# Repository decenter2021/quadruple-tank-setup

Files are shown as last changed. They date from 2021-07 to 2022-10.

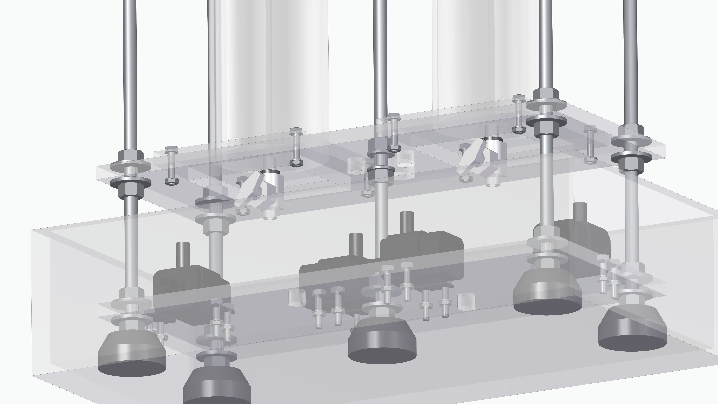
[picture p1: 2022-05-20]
cad-quadruple-tank/renders/quadruple_tank_assembly_render_10.jpg

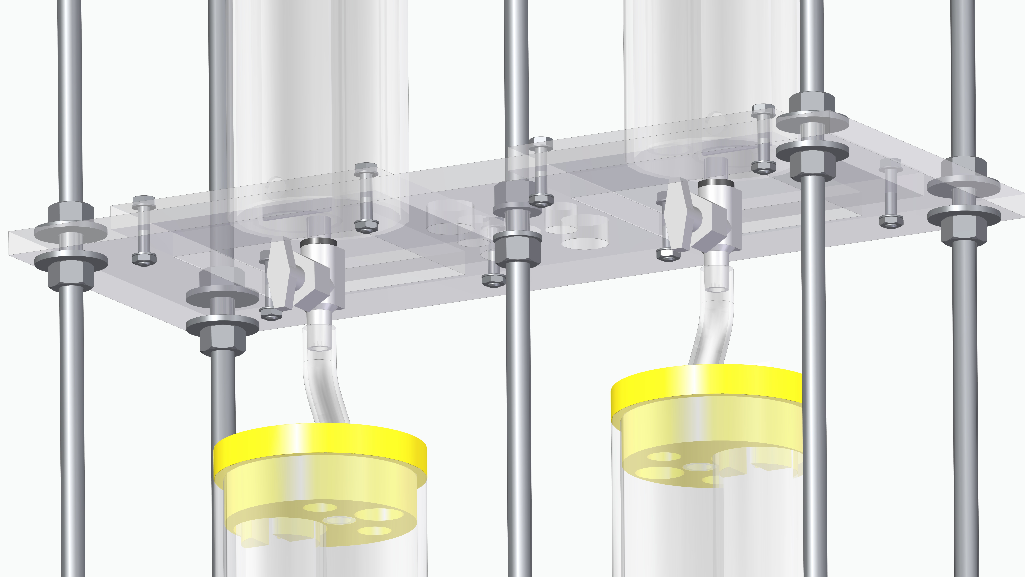
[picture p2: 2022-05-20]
cad-quadruple-tank/renders/quadruple_tank_assembly_render_09.jpg

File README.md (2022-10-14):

# Quadruple-Tank Setup <br><sub> ⚗️ Reproducible Low-cost Flexible Quadruple-Tank Process Experimental Setup for Control Educators, Practitioners, and Researchers</sub> 




 |    
:-------------------------:|:-------------------------:
CAD model             |  Physical implementation

***
## 🎯 Features
- 💻 User-friendly dedicated **MATLAB/Simulink** interface with a personal computer<br>
- 📈 Seamless shift between a **numeric simulation** and the **interface** with the real experimental plant<br>
- 💰 **Inexpensive** materials and **fast assembly** <br>
- 🔓 **Open-source** <br>
  - **CAD** models
  - Technical drawings
  - Wiring schematics
  - **PCB** design
  - **MATLAB/Simulink** interface
  - Assembly tutorials
- ⛳️ Several application **examples**
- 👩‍🔬 Suitable for control **education** in
  - System **identification**
  - **Frequency/time** response
  - State **feedback** (e.g root locus)
  - **P**, **PI**, and **PID** controllers
  - **Ziegler-Nichols** tuning procedure
  - **Disturbance** rejection
  - **Multivariate** control (e.g. LQR)
  - Effect of the position and direction of **zeros** (e.g. non-minimum phase zeros)
  - **Nonlinear** control
  - **Decentralized** control

***
## 🚀 Index

- 💡 [Description](#-description)
- ✍🏼 [Authors](#-authors)
- 📞 [Contact](#-contact)
- 📚 [Manual](#-manual)
- 🧐 [Identification](#-identification)
- ⛳️ [Examples](#%EF%B8%8F-examples)
- ⚙️ [Parts list](#%EF%B8%8F-parts-list)
- ✨ [Contributing](#-contributing)
- 📄 [License](#-license)
- 💥 [References](#-references)

***

## 💡 Description

The major hurdle in accessing laboratory experimentation is the <b>cost of acquiring experimental scientific equipment</b>, which is unbearable for many institutions. This repository provides the community of control <b>educators, practitioners, and researchers</b> with an <b>open-source low-cost</b> experimental setup and dedicated interface, which is <b>flexible</b> and very <b>easily reproducible</b>. 

<p align="justify">
The Quadruple-Tank Setup is thoroughly described in 
</p>
<p align="justify">
<a href="https://www.sciencedirect.com/science/article/pii/S0959152422001524">L. Pedroso, P. Batista, Reproducible low-cost flexible quadruple-tank process experimental setup for control educators, practitioners, and researchers, Journal of Process Control. 118 (2022) 82–94.</a>  | <a href="https://github.com/decenter2021/quadruple-tank-setup/files/9508256/lpedroso_pbatista_jpc.pdf">[Download PDF]</a>
</p>

If you use this repository, please [reference](#-references) the publication above.

The community is encouraged to [contribute](#-contributing) with application examples and suggest improvements.
***

## ✍🏼 Authors 
Leonardo Pedroso<sup>1</sup>  <a href="https://orcid.org/0000-0002-1508-496X">ORCID iD icon</a> <a href="https://github.com/leonardopedroso">ORCID iD icon</a><br>
Pedro Batista<sup>1</sup>  <a href="https://orcid.org/0000-0001-6079-0436">ORCID iD icon</a><br>

<sub>*<sup>1</sup>Institute for Systems and Robotics, Instituto Superior Técnico, Universidade de Lisboa, Portugal<br>*</sub>

***

## 📞 Contact
This repository is currently maintained by Leonardo Pedroso (<a href="mailto:leonardo.pedroso@tecnico.ulisboa.pt">leonardo.pedroso@tecnico.ulisboa.pt</a>).

***

## 📚 Manual

The **simulink block** for interfacing with the quadruple-tank process experimental network is shown below. The **inputs and outputs** are thoroughly described in <a href="#-references">(Pedroso and Batista, 2022)</a>. 

<p align="center">
 
 </p>

To create a **new model** to control the quadruple-tank experimental setup, follow these steps:
- Copy and paste the interface block in a new Simulink model;
- Copy and paste, in the directory of the new Simulink model, the file: 
  - `quadrupleLoadParameters.m`, which is executed on the initialization callback of the interface block, that loads the physical parameters of the setup, defines the sampling period, and defines the covariance matrices of the process and sensor noise for numerical simulation;
  - `quadrupleSimObj.m`, a MATLAB System Object that numerically simulates the quadruple-tank process in discrete-time;
- Create a directory `identification` to contain the `.mat` data files generated in the [identification procedure](#-identification);
- Generate and connect to the interface block a clock signal `CLK`, whose period equals the sampling period defined in `quadrupleLoadParameters.m`;
- Setup the Simulink solver to:
  - Fixed-step;
  - Discrete; and
  - Set the "Fixed-step size" parameter to half the period of the `CLK` signal;
- Set the Simulink simulation mode to "Accelerator";
- Enable the display of the "Sorted Execution Order" of Simulink to ensure the first step of the feedback loop is the water level measurement and the last is the update of the input to the pumps. Most of the time this is ensured, due to the default priorities of the inner blocks of the interface block, otherwise set the priorities of the feedback loop blocks appropriately.

***

## 🧐 Identification

The **proposed identification** procedures are detailled in what follows. For the detailled equations and physical principles used to estimate the parameters of the experimental setup making use of data gathered during these procedures see <a href="#-references">(Pedroso and Batista, 2022)</a>. 

>**Note**
> 
> **MATLAB live scripts** detailing the **identification procedure** as well as the **post-processing** of the data to estimate the model parameters are avialable at [simulink/identification](https://github.com/decenter2021/quadruple-tank-setup/tree/master/simulink/identification)

### 1. Section area of each tank

The proposed procedure is the following: 
- measure the weight of the empty tank, $w_1$ (one may want to add a little of water at the beginning for the water level to reach the scale at a water level $h_1$)
- pour water in each tank until almost full
- measure the weight of the tank with the water, $w_2$;
- measure the corresponding water level, $h_2$;
- then compute $A = (w_2-w_1)/\left(\rho(h_2-h_1)\right)$, where $\rho$ is the water density. 

The MATLAB live script `identification_1_A.mlx` corresponding to this identification procedure is available at [simulink/identification](https://github.com/decenter2021/quadruple-tank-setup/tree/master/simulink/identification).

### 2. Characteristic slope of the water level sensors

The proposed procedure to determine $dh/dr$ is the following: 
- open `identification_sl.slx` 

and for each tank: 

1. block the outlet of tank;
2. pour some water to the tanks with the pumps using the sliders in the Simulink model;
3. measure $r$ in the Simulink scope and the water level in the sensor ruler $h^{\star}$;
4. repeat 2. and 3. increasing the water level and measuring the pairs $(r,h^{\star})$, until enough samples are taken;
5. compute an estimate of $dh/dr$ performing a linear regression of the samples taken.

The plot of the data points and linear regression for an illustrative identification procedure is depicted in  <a href="#-references">(Pedroso and Batista, 2022)</a>. 

The MATLAB live script `identification_2_dh_dr.mlx` corresponding to this identification procedure is available at [simulink/identification](https://github.com/decenter2021/quadruple-tank-setup/tree/master/simulink/identification).

### 3. Response of the pumps and the fraction of the flow that is diverted on the three way valves

The following procedure is proposed:
- open `identification_sl.slx`

and for each pump (the following steps are exemplified for pump 1):
1. block the outlets of the lower tanks; 
2. send a constant PWM input to pump 1; 
3. wait until tank 1 is almost full, then turn off the pump;
4. let tank 4 pour all the water into tank 2, whose outlet should still be blocked; 
5. measure the height of the tanks 1 and 2 and, in the scope, measure the interval of time the pump was on;
6. repeat 2., 3., 4., and 5. for various PWM values. 

> **Warning**: 
> 
> The pumps are more sensitive to low PWM values, so a greater sample density in this region is beneficial. 

From each sample taken:
- one can compute the total volume of water that was pumped, $q = h_1A_1+h_2A_2$;
- the fraction of the flow that was directed to the lower tank, $\gamma = h_1A_1/(h_1A_1+h_2A_2)$. 
 
It is then possible to estimate $c_1,c_2,c_3,$ and $k$ from a nonlinear least squares regression, for instance, of model (3) in <a href="#-references">(Pedroso and Batista, 2022)</a>. 

>**Note**
>
> Although this procedure is similar for the disturbance pumps, it is necessary to keep in mind that their identification depends on the height of the disturbance flow outlet. 

The plot of the data points and linear regression for an illustrative identification procedure is depicted in  <a href="#-references">(Pedroso and Batista, 2022)</a>. 

The MATLAB live script `identification_3_pump.mlx` corresponding to this identification procedure is available at [simulink/identification](https://github.com/decenter2021/quadruple-tank-setup/tree/master/simulink/identification).

### 4. Outlet area $a$ and datum height $h_0$ of the tanks

The proposed procedure to determine $a$ and $h_0$ is the following:
- open `identification_sl.slx`
 
and for each tank:
- measure the steady-state resistor ratio value $r$ for various constant input actions $u$;
- estimate $\alpha$ and $\beta$ from the linear regression of the samples $(r,u^2)$;
- compute $a$ and $h_0$ making use of (6) in <a href="#-references">(Pedroso and Batista, 2022)</a>. 

The MATLAB live script `identification_4_a.mlx` corresponding to this identification procedure is available at [simulink/identification](https://github.com/decenter2021/quadruple-tank-setup/tree/master/simulink/identification).

***

## ⛳️ Examples

<p align="justify">
The source files of the applications described in <a href="#-references">(Pedroso and Batista, 2022)</a> are available in this repository. Their execution is shown for a prototype in the videos linked below. Access the full playlist <a href="https://www.youtube.com/playlist?list=PLj6JXRV4qcgboMBOonhQY3f7nb1WQ0N1v">here</a>.
</p>

Description             |  Video
:-------------------------:|:-------------------------:
Promotional video | 
PI Control Example | 
Frequency Response Example | 
LQR Control Example | 
Decentralized LQR Control Example | 
3D Printed Valve Assembly Tutorial | 

***

## ⚙️ Parts list

The full parts list is availble in **spreadsheet** format in [bill-of-materials/bill-of-materials.xlsx](https://github.com/decenter2021/quadruple-tank-setup/tree/master/bill-of-materials). 

Below the parts are listed among categories, with correponding cost as of **2021**. The total cost is **under 650€**.

### 💎 Acrylic

Part | Technical drawing  | Quantity | Total cost
:---|:---|:---:|:---:
Reservoir | [bottom_tank.pdf](https://github.com/decenter2021/quadruple-tank-setup/tree/master/cad-quadruple-tank/technical-drawings/bottom_tank.pdf) | 1 | 39€
Cylindrical tank with base | [tank_small.pdf](https://github.com/decenter2021/quadruple-tank-setup/tree/master/cad-quadruple-tank/technical-drawings/tank_small.pdf) / [tank_large.pdf](https://github.com/decenter2021/quadruple-tank-setup/tree/master/cad-quadruple-tank/technical-drawings/tank_large.pdf) | 4 | 133€
Slab \#1 | [slab_1.pdf](https://github.com/decenter2021/quadruple-tank-setup/tree/master/cad-quadruple-tank/technical-drawings/slab_1.pdf) | 1 | 8€
Slab \#2 | [slab_2.pdf](https://github.com/decenter2021/quadruple-tank-setup/tree/master/cad-quadruple-tank/technical-drawings/slab_2.pdf) | 1 | 8€
Slab \#3 | [slab_3.pdf](https://github.com/decenter2021/quadruple-tank-setup/tree/master/cad-quadruple-tank/technical-drawings/slab_3.pdf) | 1 | 8€
Slab \#4 | [slab_4.pdf](https://github.com/decenter2021/quadruple-tank-setup/tree/master/cad-quadruple-tank/technical-drawings/slab_4.pdf) | 1 | 8€
Slab \#5 | [slab_5.pdf](https://github.com/decenter2021/quadruple-tank-setup/tree/master/cad-quadruple-tank/technical-drawings/slab_5.pdf) | 1 | 8€
Cylindrical tube for sensor support | [sensor_tube.pdf](https://github.com/decenter2021/quadruple-tank-setup/tree/master/cad-quadruple-tank/technical-drawings/sensor_tube.pdf) | 4 | 11€

### 🔩 Structural

Part | Quantity | Total cost
:---|:---:|:---:
Zinc-plated threaded steel rod M8 x 1000mm | 5 | 5€
ISO 4034 - M8 Hexagon Nut | 60 | 2€
ISO 7093 - 8 Washer | 45 | 9€
ISO 7091 - 8 Washer | 15 | 2€
ISO 4015 - M4 x 20mm Hexagon Head bolt  | 32 | 3€
ISO 4035 - M4 Hexagon thin nuts chamfered | 32 | 2€
ISO 7092 - 4 Washer  | 64 | 3€
M3 x 15mm Hex Spacer Female-Female | 12 | 3€	
ISO 7045 - M3 x 14mm bolt | 12 | 2€
ISO 7045 - M3 x 6mm bolt | 12 | 2€
Transparent flexible tubing 8mm x 11mm x 5000mm | 1 | 6€
Transparent flexible tubing 12mm x 16mm x 5000mm | 1 | 10€
Suction cup | 2 | 2€
Rubber Washer 8mm x 14mm x 2mm |  2 | 0.5€
Rubber Washer 9mm x 14mm x 2mm | 4 | 1€
Rubber Washer 8mm x 12mm x 2mm | 4 | 1€
Teflon tape 12 m | 2 | 1€

### 🖨️ 3D printed 

Part | Solid Edge part file | Quantity | Total cost
:---|:---|:---:|:---:
Rod support | [rod_base.par](https://github.com/decenter2021/quadruple-tank-setup/tree/master/cad-quadruple-tank/3d-printing-parts) | 5 | 1.5€
Nut (Three-way valve) | [nut_diverting.par](https://github.com/decenter2021/quadruple-tank-setup/tree/master/cad-quadruple-tank/3d-printing-parts) | 2 | 0.5€ 
Pin (Three-way valve) | [regulator_pin_diverting.par](https://github.com/decenter2021/quadruple-tank-setup/tree/master/cad-quadruple-tank/3d-printing-parts) | 2 | 0.5€
Body (Three-way valve) | [body_diverting.par](https://github.com/decenter2021/quadruple-tank-setup/tree/master/cad-quadruple-tank/3d-printing-parts) | 2 | 1€
Nut (Upper/lower tank outlet valve) | [nutStraight.par](https://github.com/decenter2021/quadruple-tank-setup/tree/master/cad-quadruple-tank/3d-printing-parts) | 4 | 0.5€
Pin (Upper/lower tank outlet valve) | [regulator_pin3_straight.par](https://github.com/decenter2021/quadruple-tank-setup/tree/master/cad-quadruple-tank/3d-printing-parts) | 4 | 0.5€
Body (Upper tank outlet valve) | [body3_straight.par](https://github.com/decenter2021/quadruple-tank-setup/tree/master/cad-quadruple-tank/3d-printing-parts) | 2 | 0.5€
Body (Lower tank outlet valve) | [body3_straight_bottom.par](https://github.com/decenter2021/quadruple-tank-setup/tree/master/cad-quadruple-tank/3d-printing-parts) | 2 | 0.5€ 
Upper tank cap | [cap_tank_small.par](https://github.com/decenter2021/quadruple-tank-setup/tree/master/cad-quadruple-tank/3d-printing-parts) | 2 | 2€
Lower tank cap | [cap_tank_large.par](https://github.com/decenter2021/quadruple-tank-setup/tree/master/cad-quadruple-tank/3d-printing-parts) | 2 | 2€	
Sensor mount | [sensor_support.par](https://github.com/decenter2021/quadruple-tank-setup/tree/master/cad-quadruple-tank/3d-printing-parts) | 8 | 2€
Flexible tube spacer D8 | [tube_support.par](https://github.com/decenter2021/quadruple-tank-setup/tree/master/cad-quadruple-tank/3d-printing-parts) | 4 | 0.5€
Flexible tube spacer D12 | [tube_support_large.par](https://github.com/decenter2021/quadruple-tank-setup/tree/master/cad-quadruple-tank/3d-printing-parts) | 1 | 0.5€

### 🔌 Connectors

Part | Quantity | Total cost
:---|:---:|:---:
USB 2.0 A - mini USB B cable | 1 | 2€
Multifilar 0.5mm$^2$ black wire - 5m | 1 | 7€
Multifilar 0.5mm$^2$ red wire - 5m | 1 | 7€
Multifilar 0.14mm$^2$ black wire - 5m | 1 | 3€
Multifilar 0.14mm$^2$ red wire - 5m | 1 | 3€
Multifilar 0.14mm$^2$ white wire - 5m | 1 | 3€
5.5/2.1mm male DC plug | 1 | 0.5€
5.5/2.1/14mm female DC plug | 4 | 1€
NS25-G3 NINIGI plug | 2 | 0.5€
NS25-G4 NINIGI plug | 8 | 1€
NS25-G6 NINIGI plug | 3 | 0.5€
NS25-T NINIGI contact | 56 | 3€
NS25-W3P NINIGI socket | 2 | 0.5€
NS25-W4P NINIGI socket | 4 | 1€
NS25-W6P NINIGI socket | 3 | 1€
NSR-06 NINIGI plug | 2 | 0.5€
NDR-T NINIGI contact | 12 | 1.5€
10-pin 2.54mm single row female pin header | 2 | 0.5€
15-pin 2.54mm single row female pin header | 2 | 1€

### ⚡ Electronics
Part | Quantity | Total cost
:---|:---:|:---:
Arduino Nano | 1 | 7€
Continuous Fluid Level Sensor PN-12110215TC-12 | 4 | 136€
VMA421 water pump | 4 | 72€
100uF 25V electrolytic capacitor | 4 | 0.5€
L298N Dual H-Bridge Driver | 2 | 9€
ADS 1115 ADC | 2 | 20€
14VDC 2.5A 35W power supply | 1 | 21€
Bi-stable emergency button | 1 | 12€
L7805ACP voltage regulator | 1 | 3€
Custom PCB with connectors | 1 | 35€

***

## ✨ Contributing

The community is encouraged to contribute with 
- Suggestions
- Application examples

To contribute

- Open an issue ([tutorial on how to create an issue](https://docs.github.com/en/issues/tracking-your-work-with-issues/creating-an-issue))
- Make a pull request ([tutorial on how to contribute to GitHub projects](https://docs.github.com/en/get-started/quickstart/contributing-to-projects))
- Or, if you are not familiar with GitHub, [contact the authors](#-contact) 

***

## 📄 License

This work is licensed under the [Creative Commons Attribution-NonCommercial 4.0 International Public
License](https://creativecommons.org/licenses/by-nc/4.0/legalcode).



***

## 💥 References 
<p align="justify">

<a href="https://www.sciencedirect.com/science/article/pii/S0959152422001524">L. Pedroso, P. Batista, Reproducible low-cost flexible quadruple-tank process experimental setup for control educators, practitioners, and researchers, Journal of Process Control. 118 (2022) 82–94.</a> | <a href="https://github.com/decenter2021/quadruple-tank-setup/files/9508256/lpedroso_pbatista_jpc.pdf">[Download PDF]</a>
</p>

~~~BibTeX
@article{LPedrosoPBatista2022,
	title = {Reproducible low-cost flexible quadruple-tank process experimental setup for control educators, practitioners, and researchers},
	journal = {Journal of Process Control},
	volume = {118},
	pages = {82-94},
	year = {2022},
	issn = {0959-1524},
	doi = {https://doi.org/10.1016/j.jprocont.2022.08.010},
	author = {Leonardo Pedroso and Pedro Batista}
}
~~~

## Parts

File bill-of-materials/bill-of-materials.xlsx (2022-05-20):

Part number | Transparent Flexible Tubing 8mmx11mmx5000mm | Quantity | Cost | Solid Edge part file | Tecnhical drawing file/ 3D mdel for printing | Shop
Acylic Parts
1 | Water reservoir | 1 | $39.00 | bottom_tank.par | bottom_tank.pdf | Norplex
2 | Cylindrical tank with base | 4 | $133.00 | tank_small.par; tank_large.par | tank_small.pdf; tank_large.pdf | Norplex
3 | Slab #1 | 1 | $8.00 | slab_1.par | slab_1.pdf | Norplex
4 | Slab #2 | 1 | $8.00 | slab_2.par | slab_2.pdf | Norplex
5 | Slab #3 | 1 | $8.00 | slab_3.par | slab_3.pdf | Norplex
6 | Slab #4 | 1 | $8.00 | slab_4.par | slab_4.pdf | Norplex
7 | Slab #5 | 1 | $8.00 | slab_5.par | slab_5.pdf | Norplex
8 | Cylindrical tube for sensor support | 4 | $11.00 | sensor_tube.par | sensor_tube.pdf | Norplex
Structural Parts
9 | Zinc-plated threaded steel rod M8x1000mm | 5 | $5.00 |  |  | Leroy
10 | ISO 4034 - M8 Hexagon Nut | 60 | $2.00 |  |  | Leroy
11 | ISO 7093 - 8 Washer | 45 | $9.00 |  |  | Leroy
12 | ISO 7091 - 8 Washer | 15 | $2.00 |  |  | Leroy
13 | ISO 4015 - M4x20mm Hexagon Head Bolt | 32 | $3.00 |  |  | Leroy
14 | ISO 4035 - M4 Hexagon Nuts | 32 | $2.00 |  |  | Leroy
15 | ISO 7092 - 4 Washer | 64 | $3.00 |  |  | Leroy
16 | M3x15mm Hexagon Spacer Female-Female | 12 | $3.00 |  |  | Mauser (096-0979)
17 | ISO 7045 - M3x14mm Bolt | 12 | $2.00 |  |  | Mauser (092-0036)
18 | ISO 7045 - M3x6mm Bolt | 12 | $2.00 |  |  | Mauser (092-0037)
19 | Transparent Flexible Tubing 8mmx11mmx5000mm | 1 | $6.00 |  |  | Leroy
20 | Transparent Flexible Tubing 12mmx16mmx5000mm | 1 | $10.00 |  |  | Leroy
21 | Suction cup | 2 | $2.00 |  |  | Leroy
22 | Rubber Washer 8mmx14mmx2mm | 2 | $0.50 |  |  | DIY
23 | Rubber Washer 9mmx14mmx2mm | 4 | $1.00 |  |  | DIY
24 | Rubber Washer 8mmx12mmx2mm | 4 | $1.00 |  |  | DIY
25 | Teflon Tape 12m | 2 | $1.00 |  |  | Leroy
3D Printed Parts
26 | Rod support | 5 | $1.50 | rod_base.par | rod_base.3mf(.stl) | Ultimaker 2
27 | Nut (Three-way-valve) | 2 | $0.50 | nut_diverting.par | nut_diverting.3mf(.stl) | Ultimaker 2
28 | Pin (Three-way-valve) | 2 | $0.50 | regulator_pin_diverting.par | regulator_pin_diverting.par.3mf(.stl) | Ultimaker 2
29 | Body (Three-way-valve) | 2 | $1.00 | body_diverting.par | body_diverting.3mf(.stl) | Ultimaker 2
30 | Nut (Upper/lower tank outlet valve) | 4 | $0.50 | nutStraight.par | nutStraight.3mf(.stl) | Ultimaker 2
31 | Pin (Upper/lower tank outlet valve) | 4 | $0.50 | regulator_pin3_straight.par | regulator_pin3_straight.3mf(.stl) | Ultimaker 2
32 | Body (Upper tank outlet valve) | 2 | $0.50 | body3_straight.par | body3_straight.par.3mf(.stl) | Ultimaker 2
33 | Body (Lower tank outlet valve) | 2 | $0.50 | body3_straight_bottom.par | body3_straight_bottom.3mf(.stl) | Ultimaker 2
34 | Upper tank cap | 2 | $2.00 | cap_tank_small.par | cap_tank_small.3mf(.stl) | Ultimaker 2
35 | Lower tank cap | 2 | $2.00 | cap_tank_large.par | cap_tank_large.3mf(.stl) | Ultimaker 2
36 | Sensor mount | 8 | $2.00 | sensor_support.par | sensor_support.3mf(.stl) | Ultimaker 2
37 | Flexible tube spacer D8 | 4 | $0.50 | tube_support.par | tube_support.3mf(.stl) | Ultimaker 2
38 | Flexible tube spacer D12 | 1 | $0.50 | tube_support_large.par | tube_support_large.3mf(.stl) | Ultimaker 2
Electrical connectors
40 | USB 2.0 A - mini USB B cable | 1 | $2.00 |  |  | Mauser (047-0012)
41 | Multifilar 0.5mm^2 black wire - 5m | 1 | $7.00 |  |  | Mauser (016-0594)
42 | Multifilar 0.5mm^2 red wire - 5m | 1 | $7.00 |  |  | Mauser (016-0593)
43 | Multifilar 0.14mm^2 black wire - 5m | 1 | $3.00 |  |  | Mauser (016-0210)
44 | Multifilar 0.14mm^2 red wire - 5m | 1 | $3.00 |  |  | Mauser (016-0209)
45 | Multifilar 0.14mm^2 white wire - 5m | 1 | $3.00 |  |  | Mauser (016-0212)
46 | 5.5/2.1mm male DC plug | 1 | $0.50 |  |  | Mauser (011-0511)
47 | 5.5/2.1/14mm female DC plug | 4 | $1.00 |  |  | Mauser (011-0337)
48 | NS25-G3 NINIGI plug | 2 | $0.50 |  |  | Mauser (011-1319)
49 | NS25-G4 NINIGI plug | 8 | $1.00 |  |  | Mauser (011-1201)
50 | NS25-G6 NINIGI plug | 3 | $0.50 |  |  | Mauser (011-1500)
51 | NS25-T NINIGI contact | 56 | $3.00 |  |  | Mauser (011-1243)
52 | NS25-W3P NINIGI socket | 2 | $0.50 |  |  | Mauser (011-1321)
53 | NS25-W4P NINIGI socket | 4 | $1.00 |  |  | Mauser (011-1218)
54 | NS25-W6P NINIGI socket | 3 | $1.00 |  |  | Mauser (011-1487)
55 | NSR-06 NINIGI plug | 2 | $0.50 |  |  | Mauser (011-0674)
56 | NDR-T NINIGI contact | 12 | $1.50 |  |  | Mauser (011-0613)
57 | 10-pin 2.54mm single row female pin header | 2 | $0.50 |  |  | Mauser (012-0078)
58 | 15-pin 2.54mm single row female pin header | 2 | $1.00 |  |  | Mauser (012-0083)
Electrical Components Parts
59 | Arduino Nano | 1 | $7.00 |  |  | Mauser (096-8746)
60 | Continuous Fluid Level Sensor PN-12110215TC-12 | 4 | $136.00 |  |  | Mauser (096-9283), Adafruit (464)
61 | VMA421 water pump | 4 | $72.00 |  |  | Mauser (096-6116)
62 | 100uF 25V electrolytic capacitor | 4 | $0.50 |  |  | Mauser (004-0114)
63 | L298N Dual H-Bridge Driver | 2 | $9.00 |  |  | Mauser (096-6807)
64 | ADS 1115 ADC | 2 | $20.00 |  |  | Mauser (096-7616)
65 | 14VDC 2.5A 35W power supply | 1 | $21.00 |  |  | Mauser (035-3362)
66 | Bi-stable emergency button | 1 | $12.00 |  |  | Mauser (010-0662)
67 | L7805ACP voltage regulator | 1 | $3.00 |  |  | Mauser (001-9131)
68 | Custom PCB with connectors | 1 | $35.00 |  |  | G7eletronica
 |  |  | 643

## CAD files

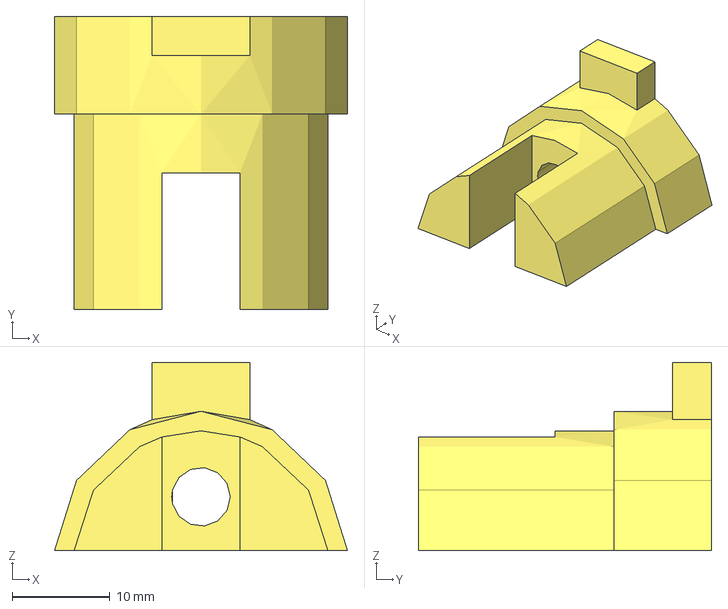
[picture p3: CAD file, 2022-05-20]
cad-quadruple-tank/3d-printing-parts/3mf/sensor_support.3mf
30.0 x 30.0 x 19.2 mm

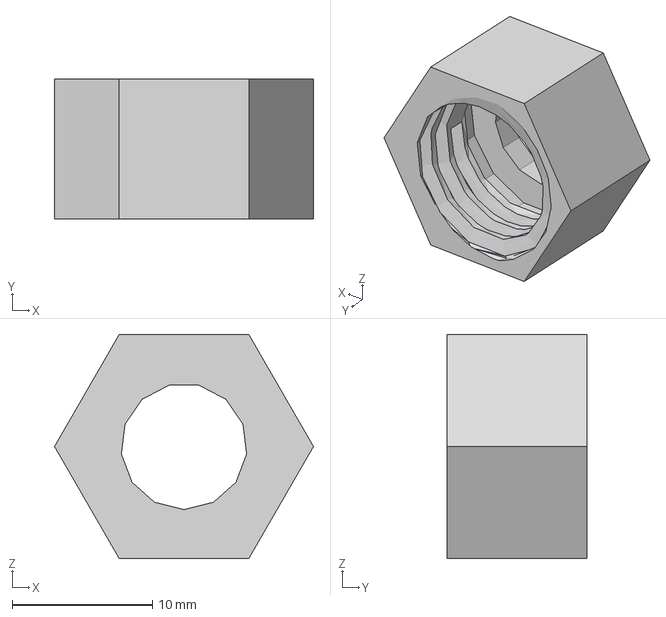
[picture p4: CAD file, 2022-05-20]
cad-quadruple-tank/3d-printing-parts/3mf/nutStraight.3mf
18.5 x 10.0 x 16.0 mm

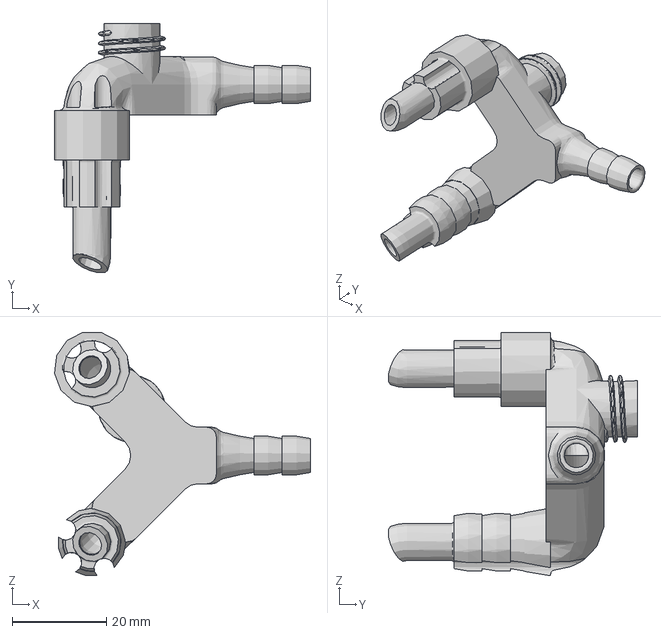
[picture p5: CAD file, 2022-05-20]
cad-quadruple-tank/3d-printing-parts/3mf/body_diverting.3mf
54.3 x 52.9 x 51.7 mm

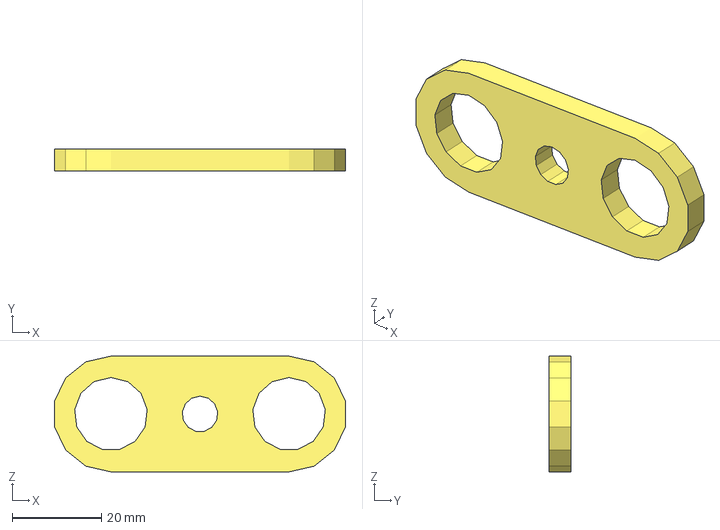
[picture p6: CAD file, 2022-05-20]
cad-quadruple-tank/3d-printing-parts/3mf/tube_support_large.3mf
65.3 x 5.00 x 26.0 mm

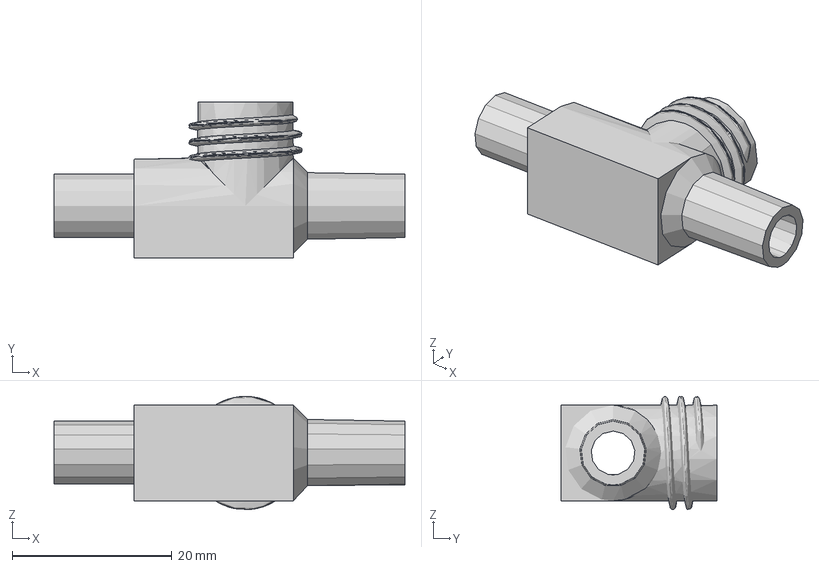
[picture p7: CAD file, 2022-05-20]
cad-quadruple-tank/3d-printing-parts/3mf/body3_straight.3mf
44.0 x 19.5 x 14.2 mm

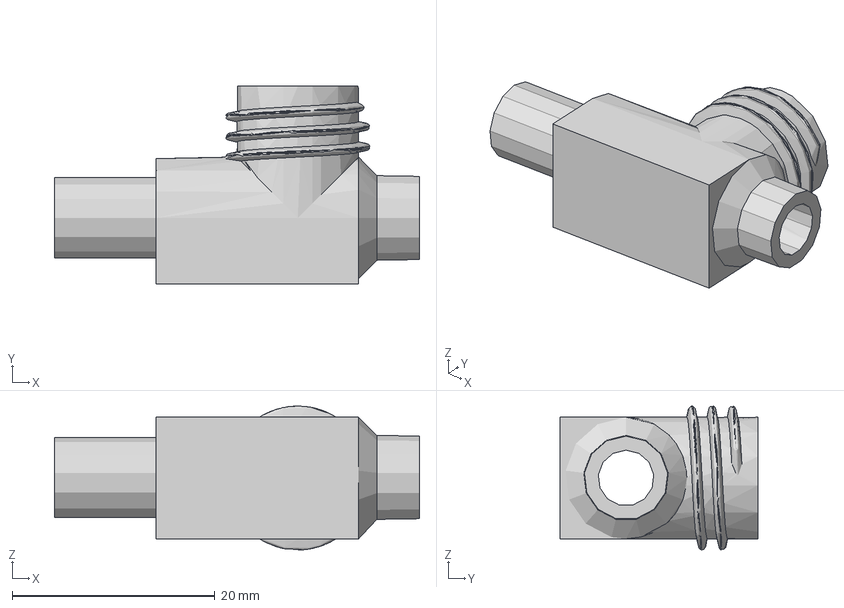
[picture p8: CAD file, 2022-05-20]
cad-quadruple-tank/3d-printing-parts/3mf/body3_straight_bottom.3mf
36.0 x 19.5 x 14.2 mm

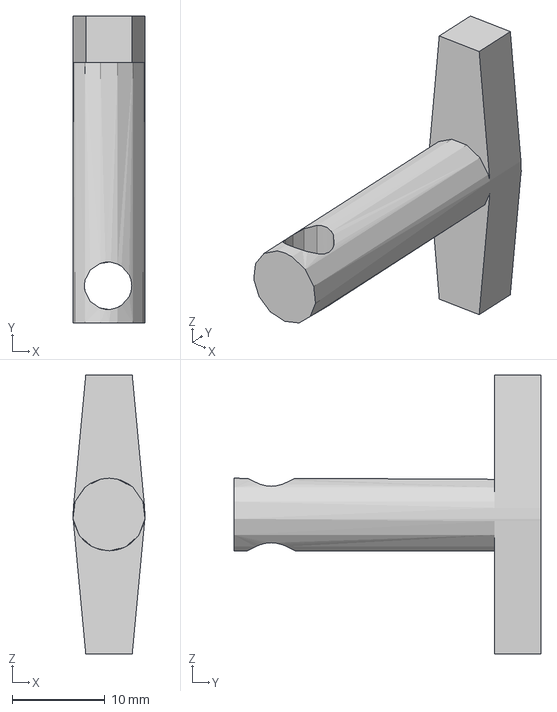
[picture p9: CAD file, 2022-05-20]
cad-quadruple-tank/3d-printing-parts/3mf/regulator_pin_diverting.3mf
7.74 x 33.0 x 30.0 mm

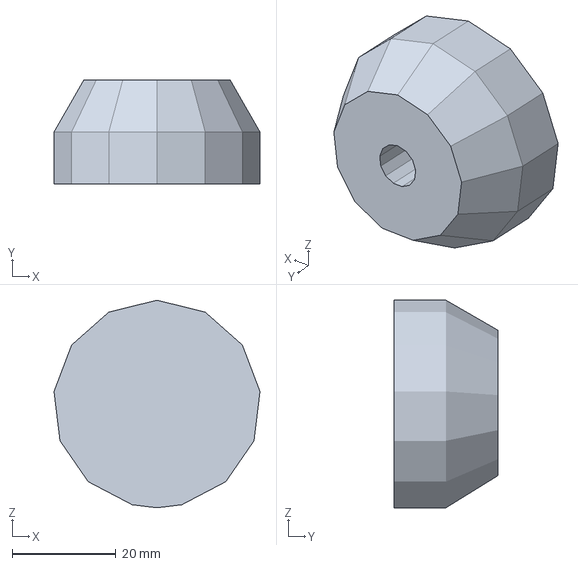
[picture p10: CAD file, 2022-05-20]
cad-quadruple-tank/3d-printing-parts/3mf/rod_base.3mf
39.7 x 20.0 x 40.0 mm

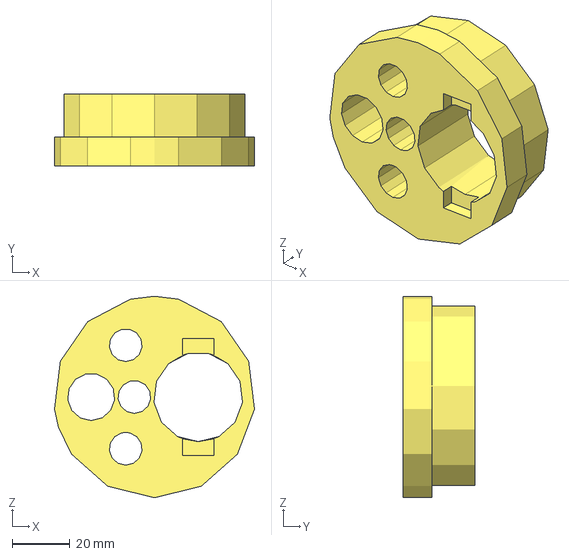
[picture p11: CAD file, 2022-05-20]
cad-quadruple-tank/3d-printing-parts/3mf/cap_tank_large.3mf
69.5 x 25.0 x 70.0 mm

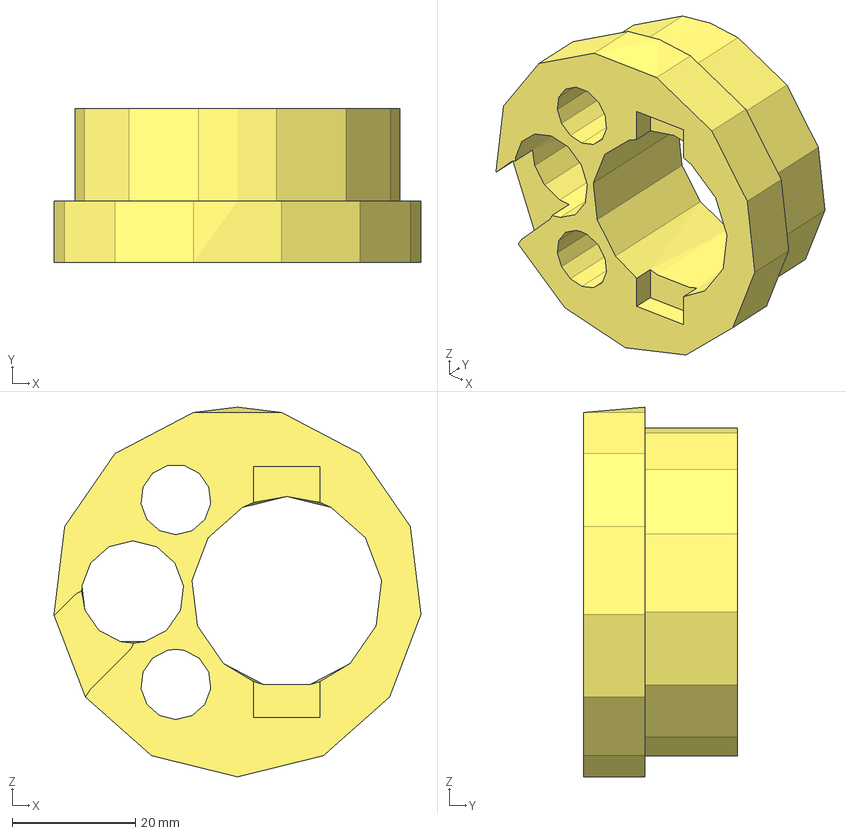
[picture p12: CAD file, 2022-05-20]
cad-quadruple-tank/3d-printing-parts/3mf/cap_tank_small.3mf
59.6 x 25.0 x 60.0 mm

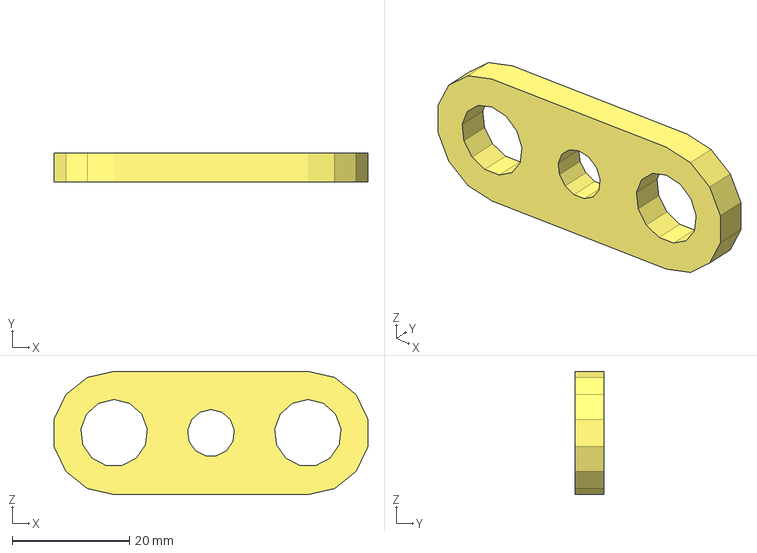
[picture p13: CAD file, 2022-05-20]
cad-quadruple-tank/3d-printing-parts/3mf/tube_support.3mf
53.5 x 5.00 x 21.0 mm

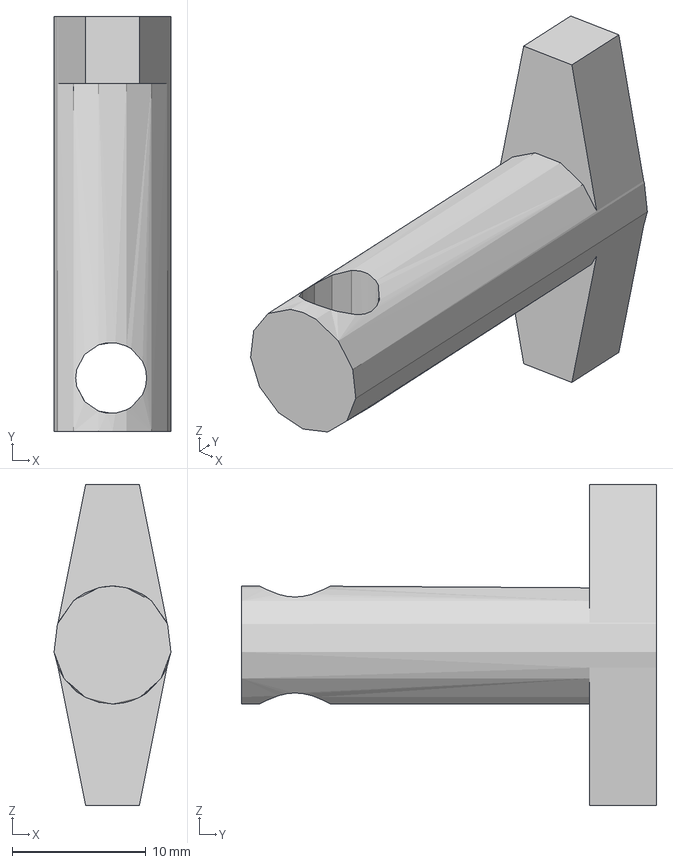
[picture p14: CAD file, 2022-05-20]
cad-quadruple-tank/3d-printing-parts/3mf/regulator_pin3_straight.3mf
8.74 x 31.0 x 24.0 mm

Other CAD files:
cad-quadruple-tank/3d-printing-parts/3mf/nut_diverting.3mf
cad-quadruple-tank/3d-printing-parts/stl/body3_straight.stl
cad-quadruple-tank/3d-printing-parts/stl/body3_straight_bottom.stl
cad-quadruple-tank/3d-printing-parts/stl/body_diverting.stl
cad-quadruple-tank/3d-printing-parts/stl/cap_tank_large.stl
cad-quadruple-tank/3d-printing-parts/stl/cap_tank_small.stl
cad-quadruple-tank/3d-printing-parts/stl/nutStraight.stl
cad-quadruple-tank/3d-printing-parts/stl/nut_diverting.stl
cad-quadruple-tank/3d-printing-parts/stl/regulator_pin3_straight.stl
cad-quadruple-tank/3d-printing-parts/stl/regulator_pin_diverting.stl
cad-quadruple-tank/3d-printing-parts/stl/rod_base.stl
cad-quadruple-tank/3d-printing-parts/stl/sensor_support.stl
cad-quadruple-tank/3d-printing-parts/stl/tube_support.stl
cad-quadruple-tank/3d-printing-parts/stl/tube_support_large.stl

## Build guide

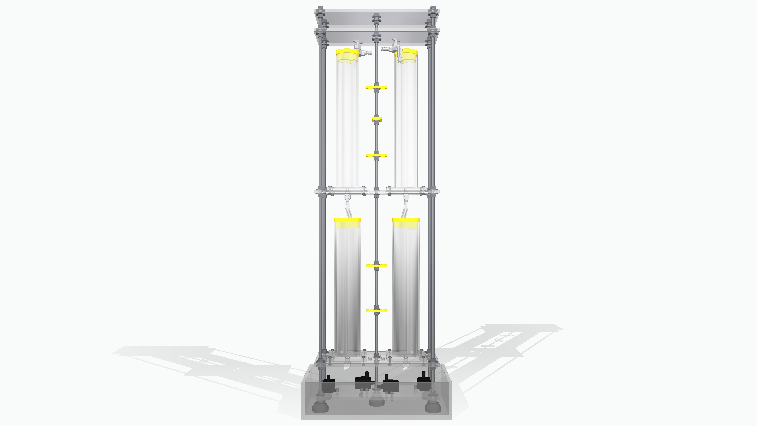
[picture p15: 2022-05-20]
cad-quadruple-tank/renders/quadruple_tank_assembly_render_00.jpg

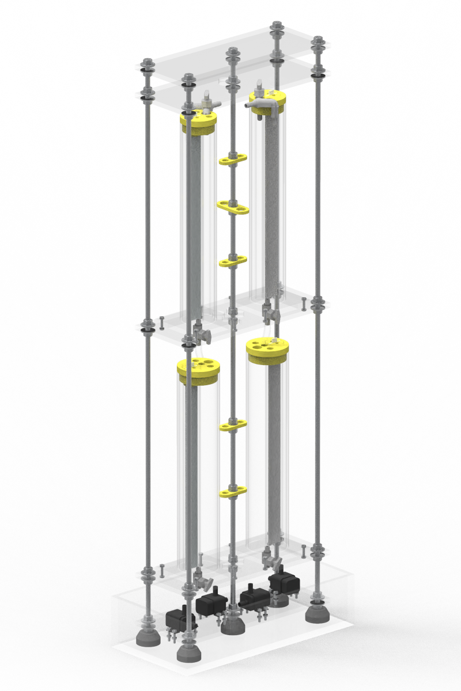
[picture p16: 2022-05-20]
cad-quadruple-tank/renders/quadruple_assembly_keyshot_render_00.png

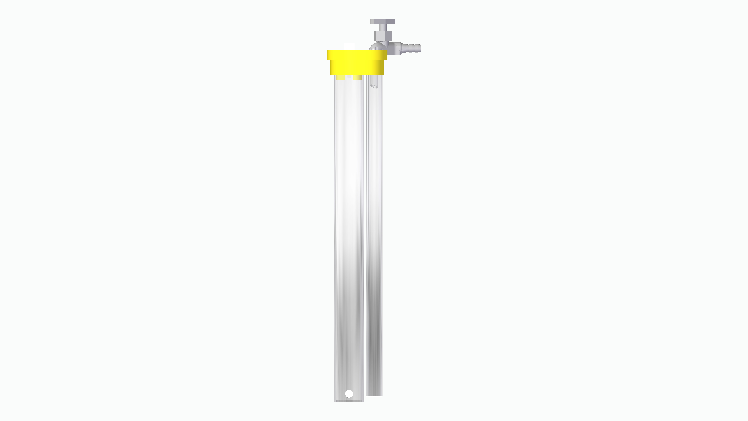
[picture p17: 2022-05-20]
cad-quadruple-tank/renders/cap_tank_small_assembly_render_00.jpg

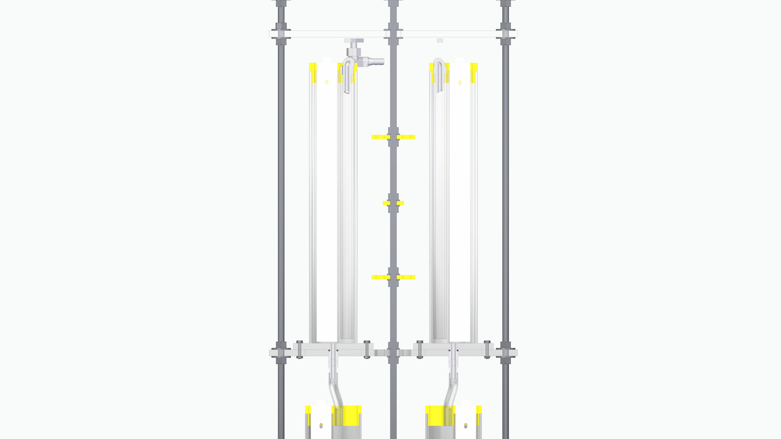
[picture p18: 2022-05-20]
cad-quadruple-tank/renders/quadruple_tank_assembly_render_07.jpg

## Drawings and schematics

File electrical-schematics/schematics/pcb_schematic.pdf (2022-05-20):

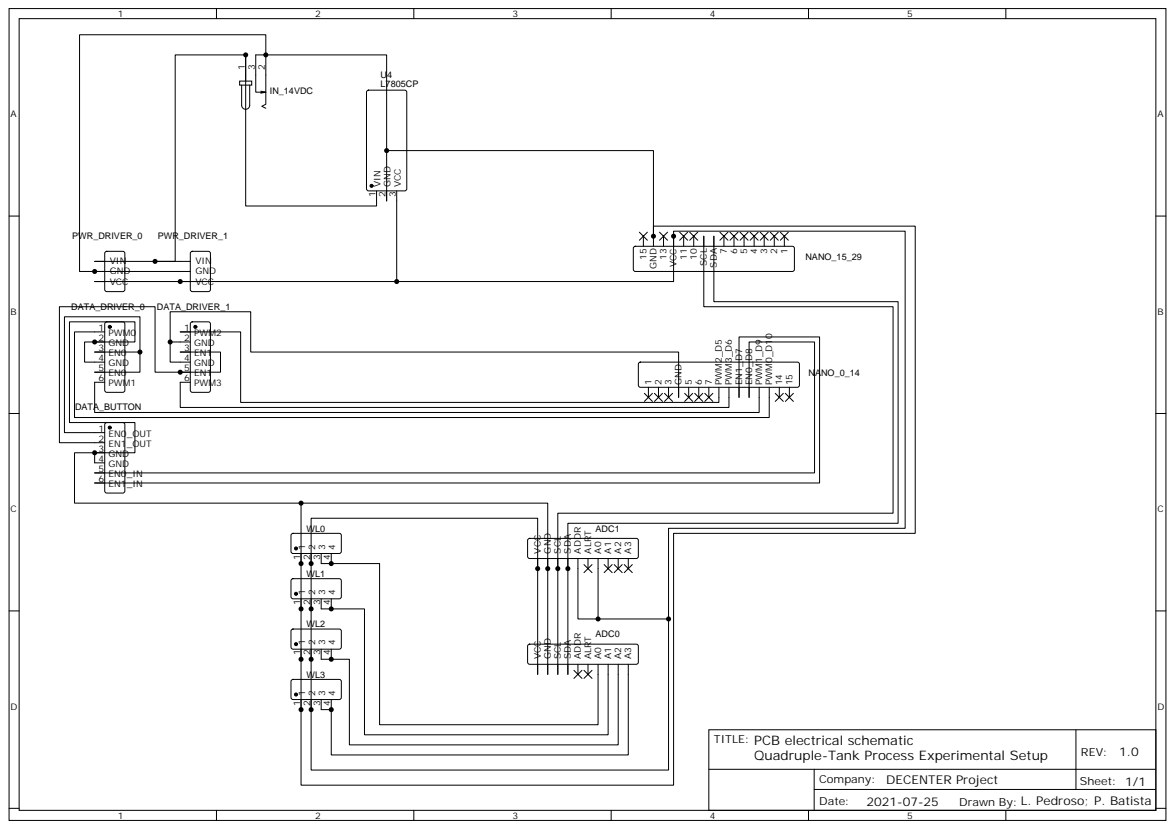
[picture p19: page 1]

TITLE: PCB electrical schematic
Quadruple-Tank Process Experimental Setup

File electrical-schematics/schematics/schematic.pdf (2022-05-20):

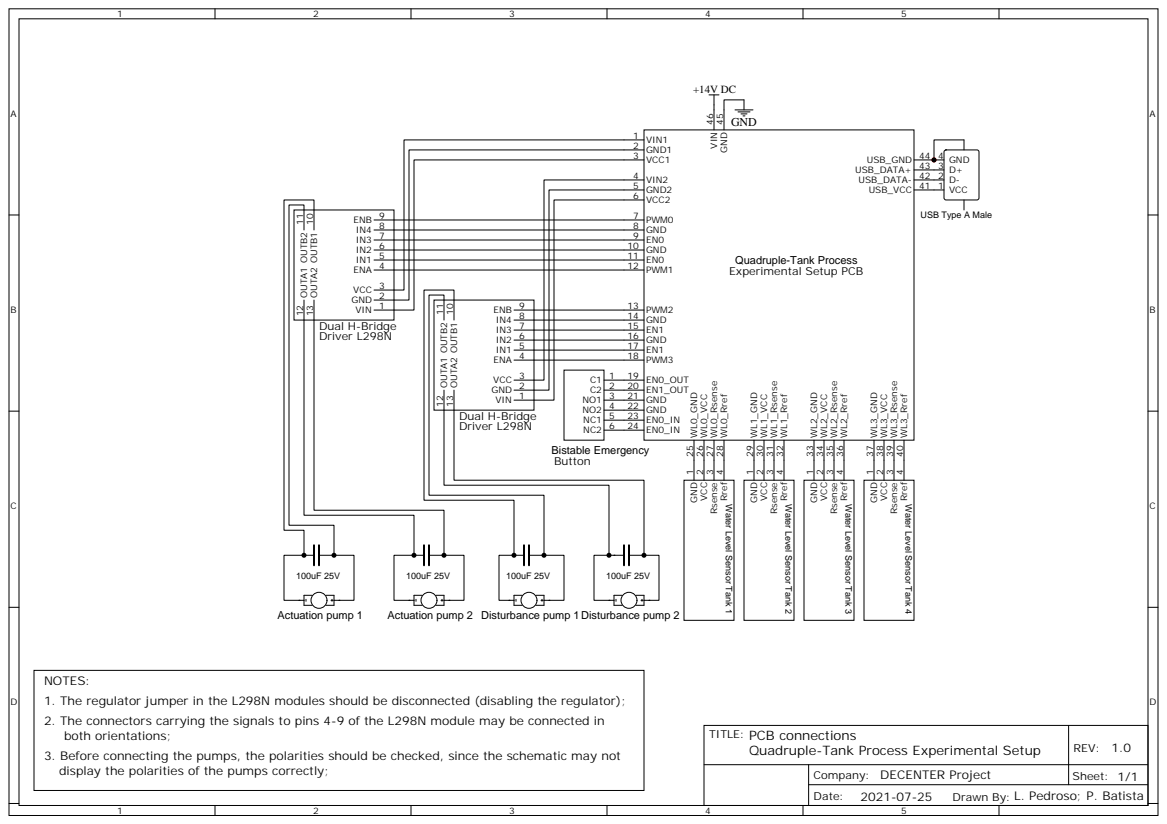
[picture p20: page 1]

Water Level Sensor Tank 1

Water Level Sensor Tank 2

Water Level Sensor Tank 3

Water Level Sensor Tank 4

NOTES:
1. The regulator jumper in the L298N modules should be disconnected (disabling the regulator);
2. The connectors carrying the signals to pins 4-9 of the L298N module may be connected in
both orientations;
3. Before connecting the pumps, the polarities should be checked, since the schematic may not
display the polarities of the pumps correctly;

TITLE: PCB connections
Quadruple-Tank Process Experimental Setup

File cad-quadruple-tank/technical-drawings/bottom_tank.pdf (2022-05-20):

D | D

6

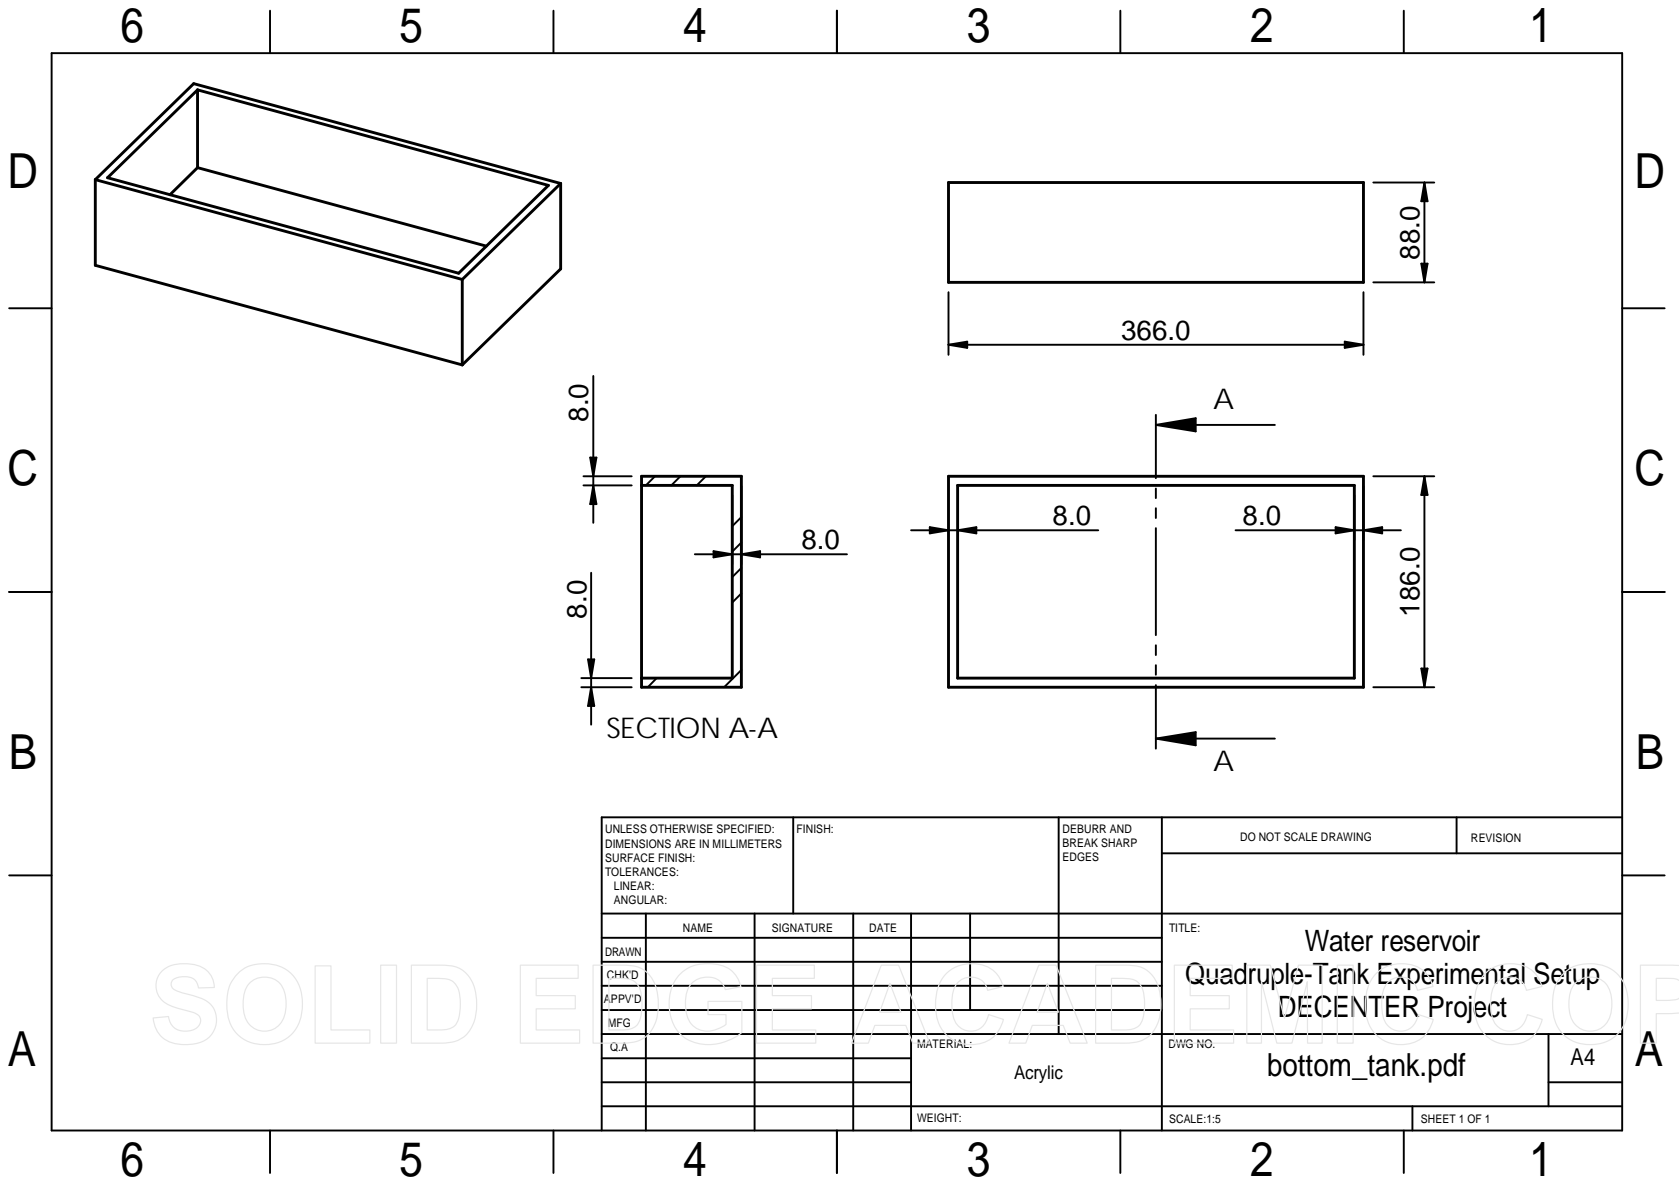
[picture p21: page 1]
FINISH:; DEBURR AND; BREAK SHARP EDGES; DO NOT SCALE DRAWING; REVISION; DWG NO.; SCALE:1:5; SHEET 1 OF 1; WEIGHT:; DECENTER Project; SECTION A-A

UNLESS OTHERWISE SPECIFIED:
DIMENSIONS ARE IN MILLIMETERS
SURFACE FINISH:
TOLERANCES:
LINEAR:
ANGULAR:

NAME | SIGNATURE | DATE | | | | TITLE: Water reservoir

DRAWN

Quadruple-Tank Experimental Setup

CHK'D

APPV'D

MFG

Q.A | | | | MATERIAL: | bottom_tank.pdf | A4 Acrylic

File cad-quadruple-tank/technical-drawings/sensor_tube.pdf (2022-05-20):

E | E
F | F

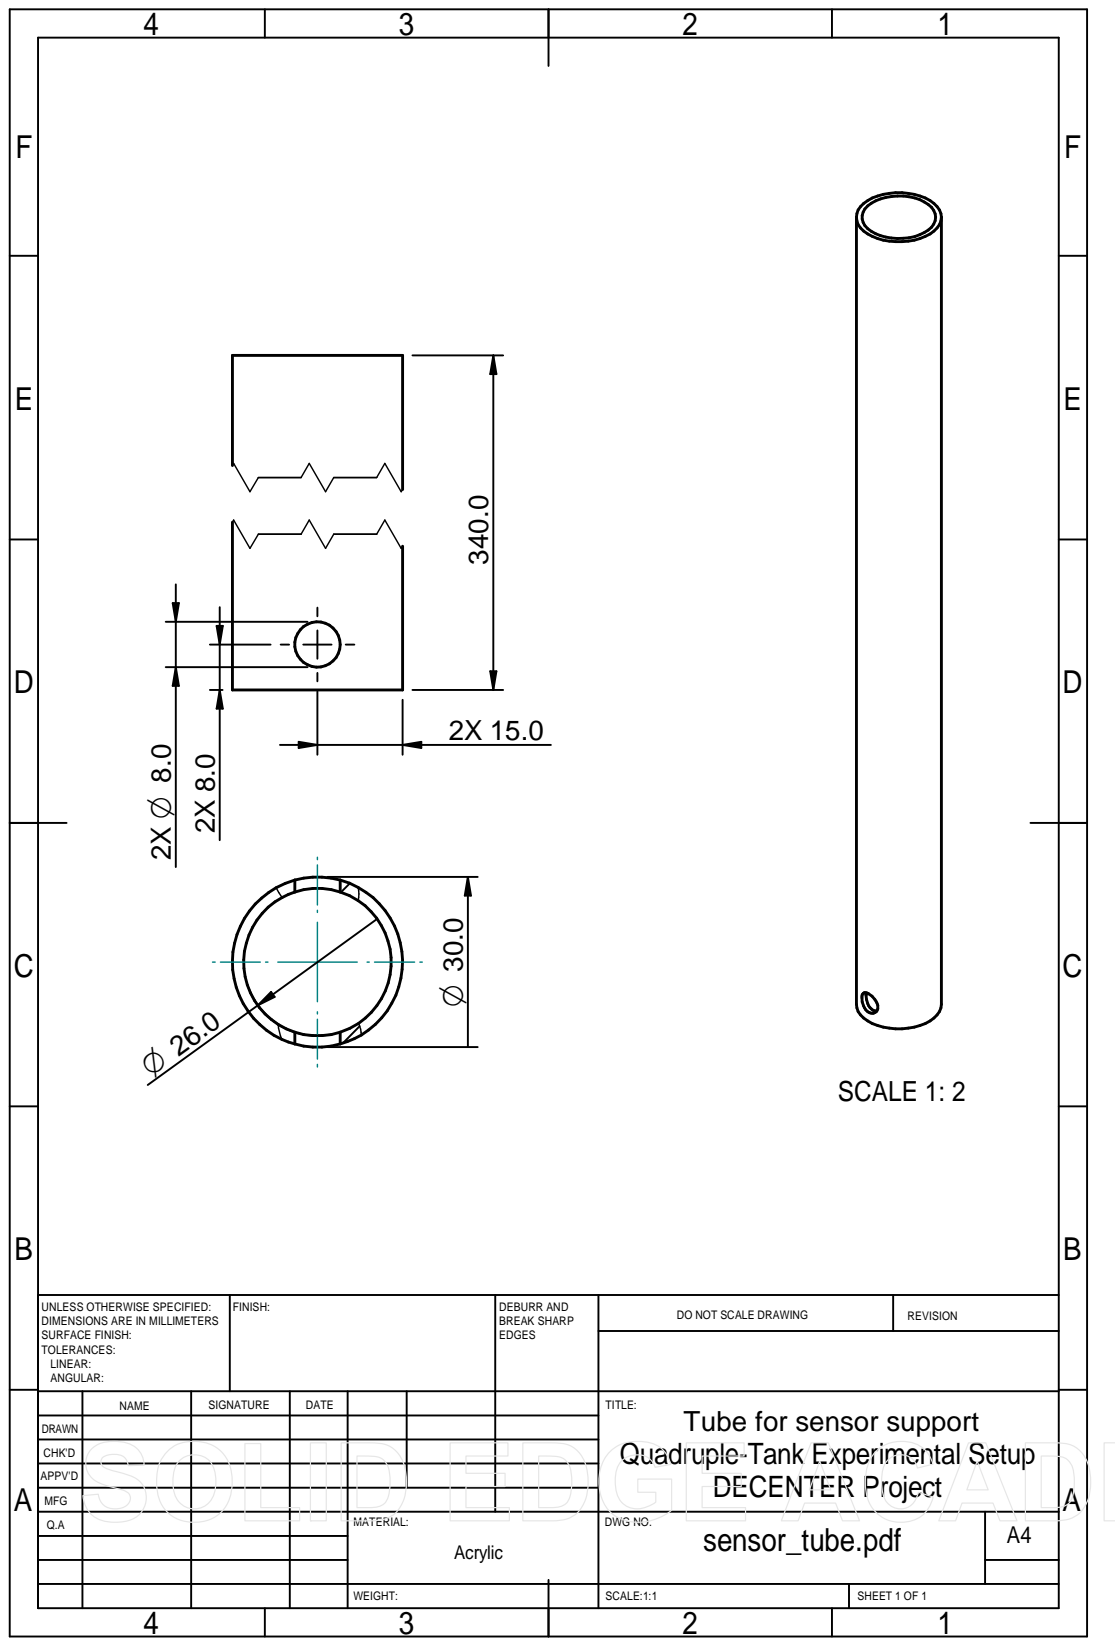
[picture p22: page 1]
SCALE 1: 2; FINISH:; DEBURR AND; BREAK SHARP EDGES; DO NOT SCALE DRAWING; REVISION; SCALE:1:1; SHEET 1 OF 1; WEIGHT:; DECENTER Project; Acrylic

UNLESS OTHERWISE SPECIFIED:
DIMENSIONS ARE IN MILLIMETERS
SURFACE FINISH:
TOLERANCES:
LINEAR:
ANGULAR:

NAME | SIGNATURE | DATE | | | | TITLE: Tube for sensor support Quadruple-Tank Experimental Setup

DRAWN

CHK'D

APPV'D

MFG

Q.A | | | | MATERIAL: | DWG NO. sensor_tube.pdf | A4

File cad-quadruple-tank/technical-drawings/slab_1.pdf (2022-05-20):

D | D

6

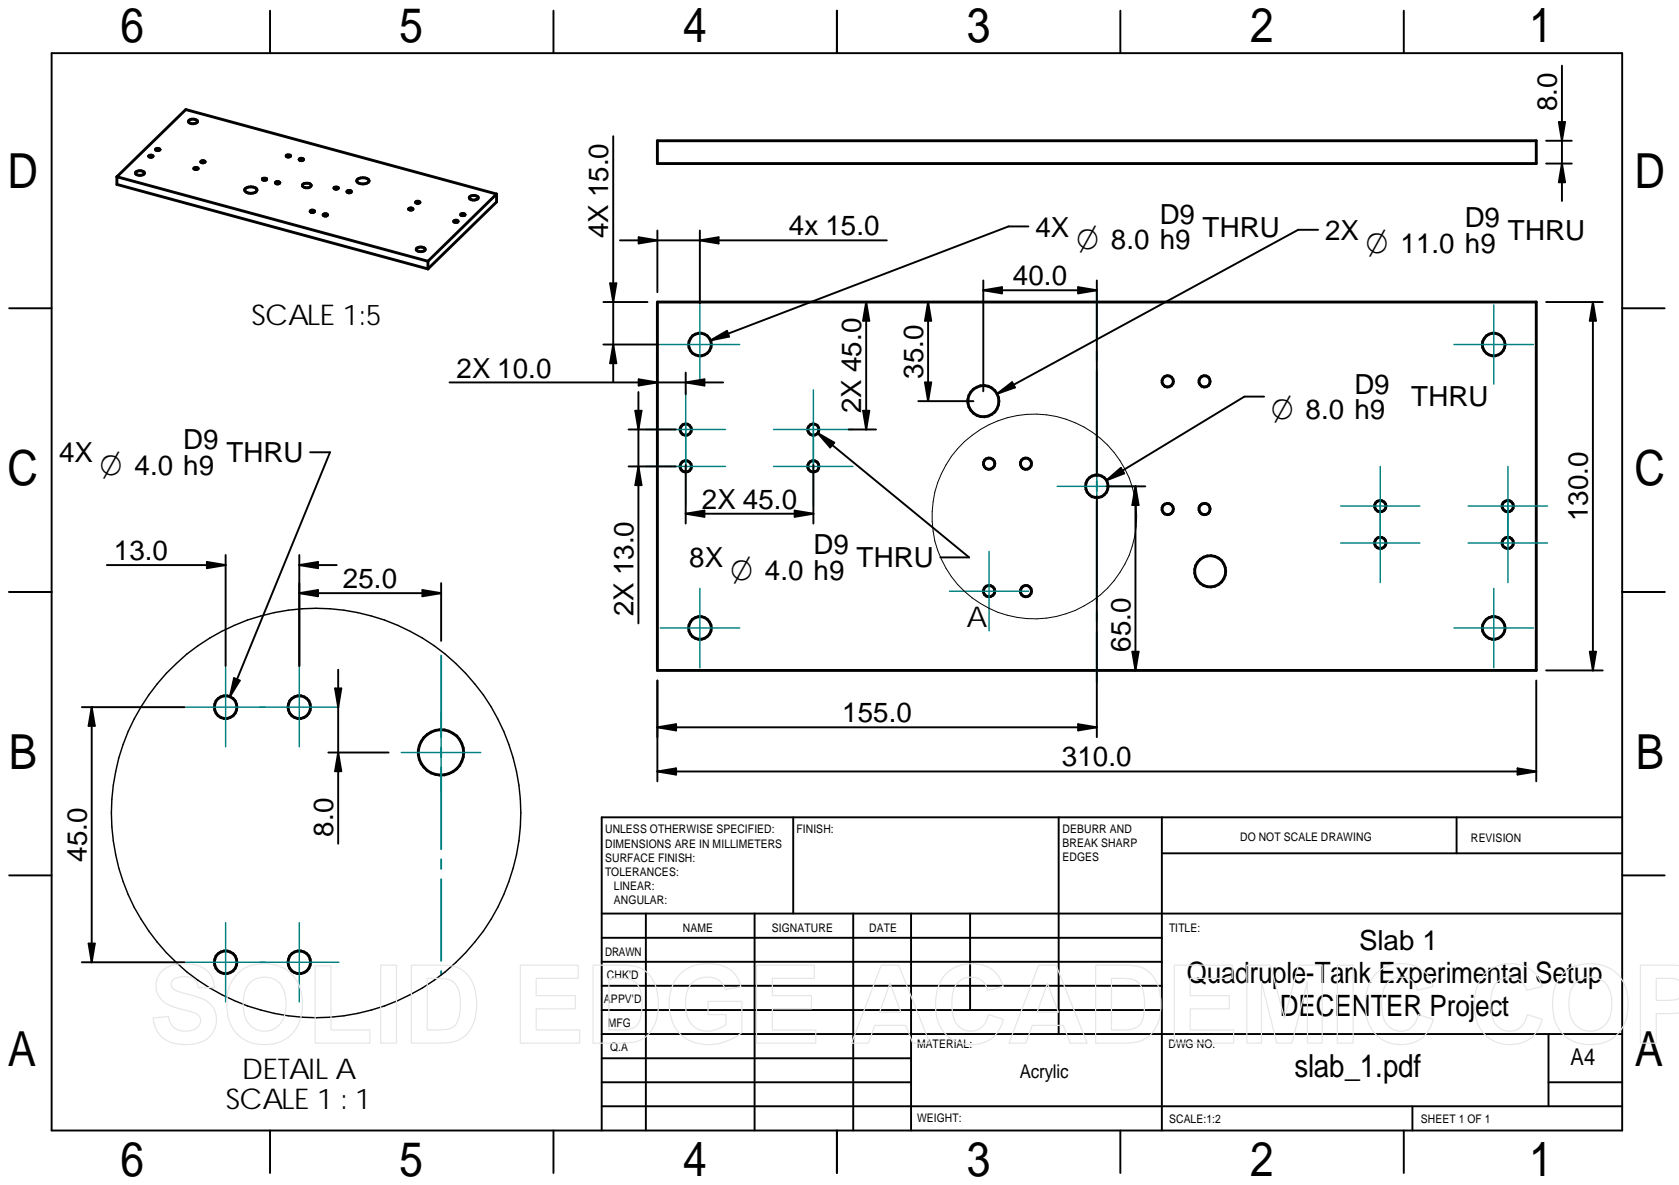
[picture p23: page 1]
FINISH:; DEBURR AND; BREAK SHARP EDGES; DO NOT SCALE DRAWING; REVISION; DWG NO.; SCALE:1:2; SHEET 1 OF 1; WEIGHT:; SCALE 1:5; DETAIL A SCALE 1 : 1; 15.0 4X 4x 15.0 O 8.0 D9 h9 4X THRU; D9 h9 THRU; THRU; DECENTER Project

UNLESS OTHERWISE SPECIFIED:
DIMENSIONS ARE IN MILLIMETERS
SURFACE FINISH:
TOLERANCES:
LINEAR:
ANGULAR:

NAME | SIGNATURE | DATE | | | | TITLE: Slab 1

DRAWN

Quadruple-Tank Experimental Setup

CHK'D

APPV'D

MFG

Q.A | | | | MATERIAL: Acrylic | slab_1.pdf | A4

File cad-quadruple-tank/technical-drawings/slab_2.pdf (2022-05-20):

D | D

6

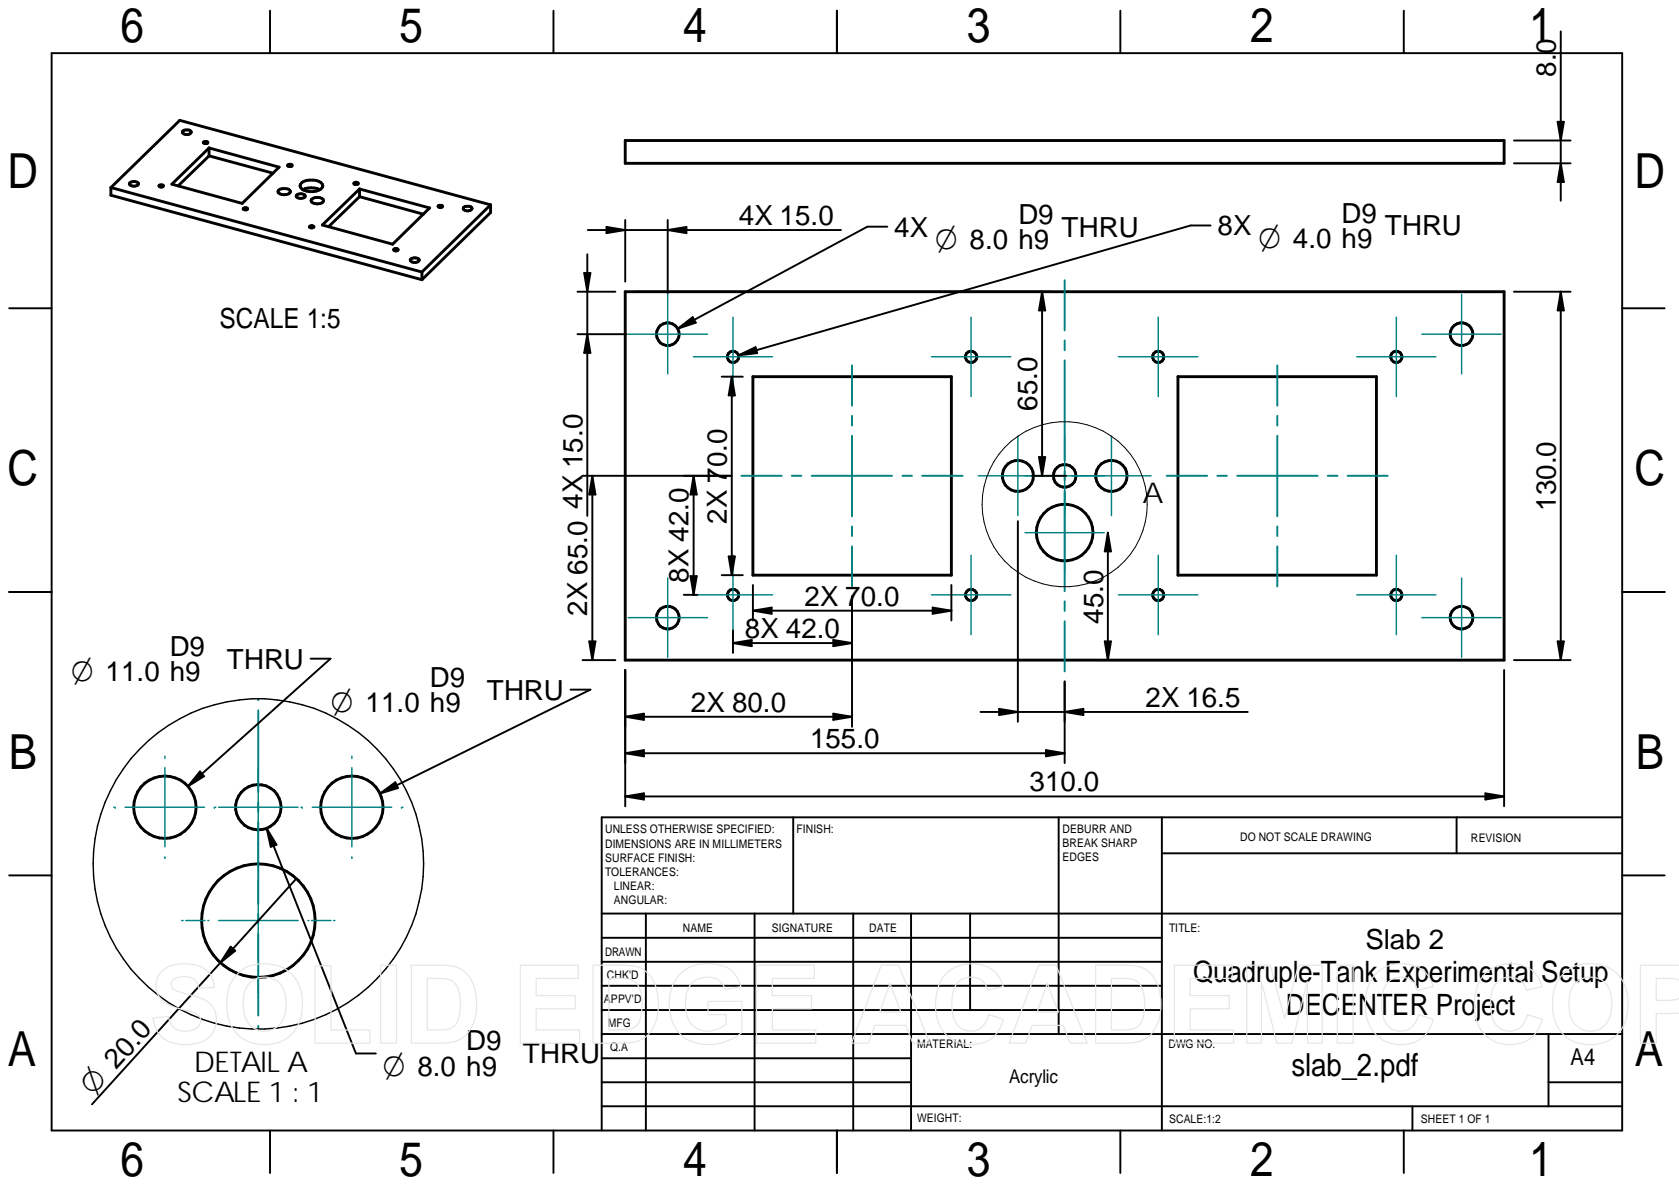
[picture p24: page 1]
SCALE 1:5; FINISH:; DEBURR AND; BREAK SHARP EDGES; MATERIAL:; DO NOT SCALE DRAWING; REVISION; DWG NO.; SCALE:1:2; SHEET 1 OF 1; WEIGHT:; DETAIL A SCALE 1 : 1; THRU; D9 h9 THRU; h9 THRU O ²⁰.0; Acrylic; DECENTER Project; slab_2.pdf

UNLESS OTHERWISE SPECIFIED:
DIMENSIONS ARE IN MILLIMETERS
SURFACE FINISH:
TOLERANCES:
LINEAR:
ANGULAR:

NAME | SIGNATURE | DATE | TITLE: Slab 2

DRAWN

Quadruple-Tank Experimental Setup

CHK'D

APPV'D

MFG

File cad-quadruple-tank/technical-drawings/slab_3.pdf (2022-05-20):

D | D

6

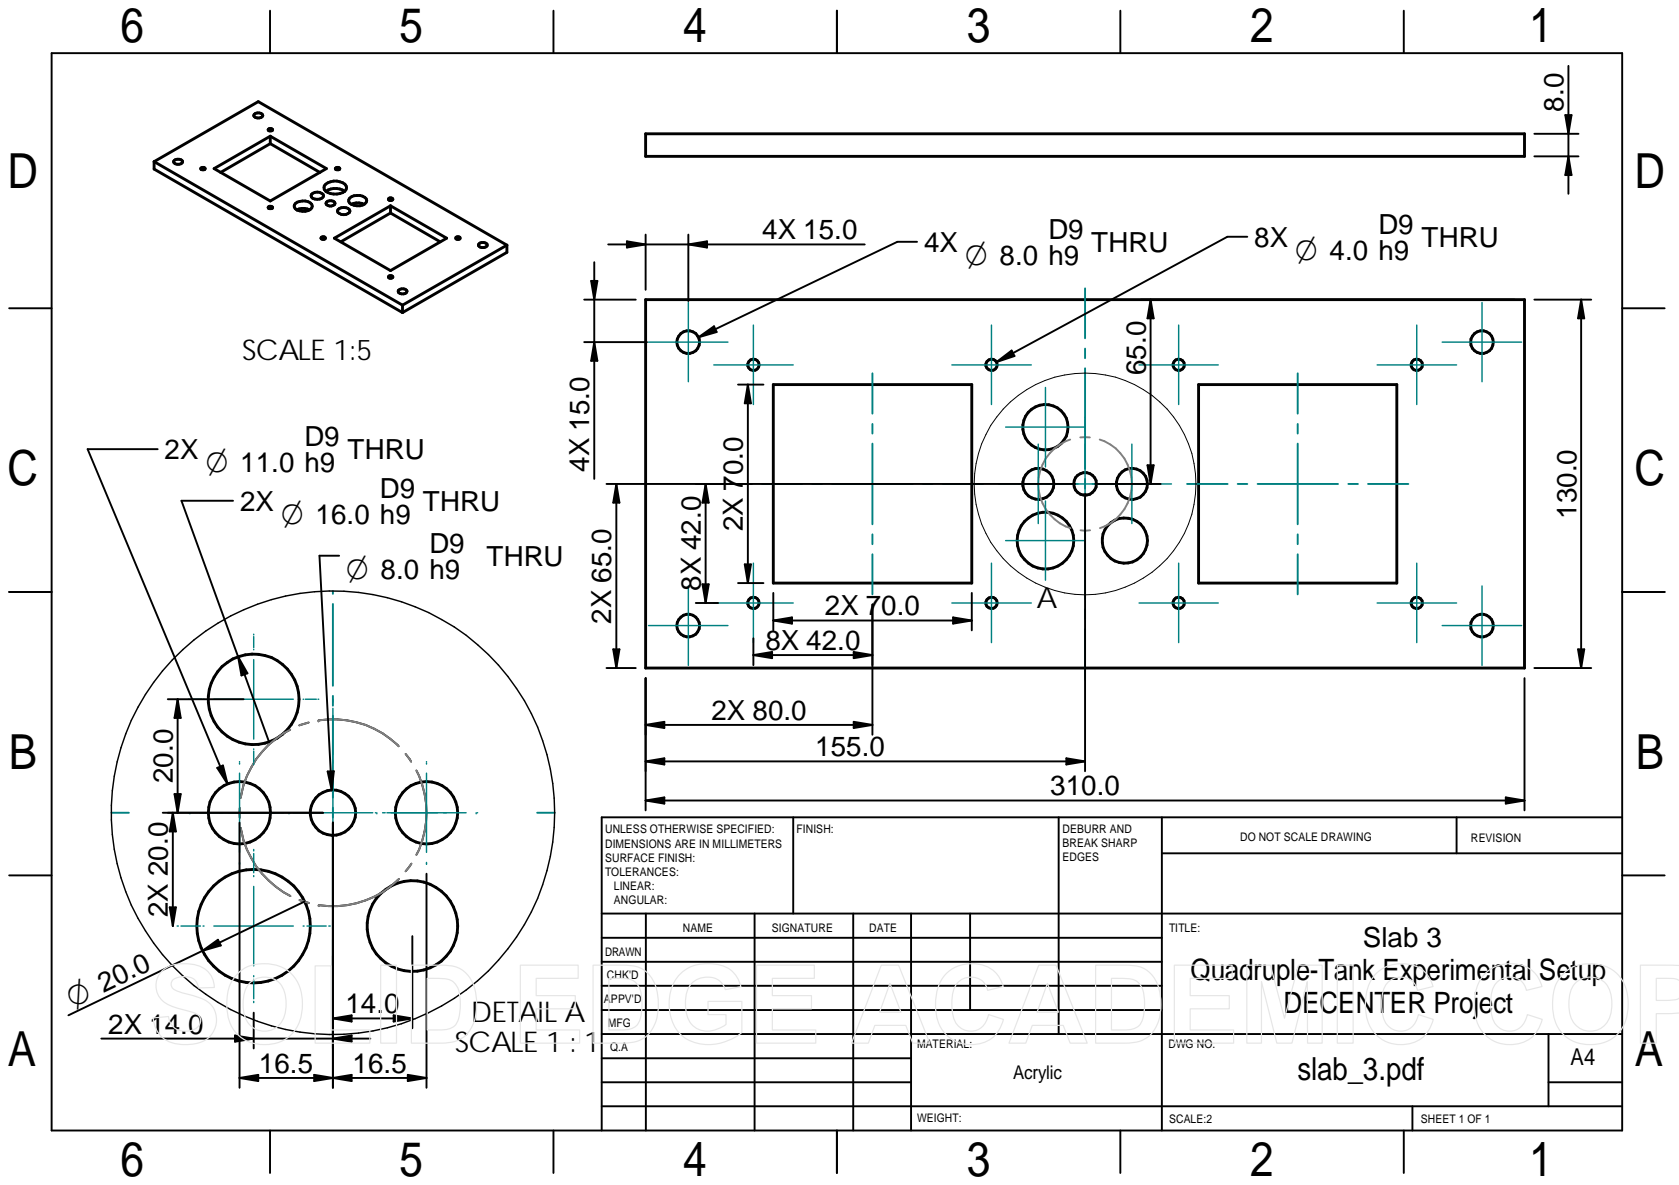
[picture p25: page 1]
CHK'D; FINISH:; DEBURR AND; BREAK SHARP EDGES; DO NOT SCALE DRAWING; REVISION; DWG NO.; SCALE:2; SHEET 1 OF 1; WEIGHT:; SCALE 1:5; DETAIL A SCALE 1 : 1; THRU; D9 h9 THRU; DECENTER Project; slab_3.pdf

UNLESS OTHERWISE SPECIFIED:
DIMENSIONS ARE IN MILLIMETERS
SURFACE FINISH:
TOLERANCES:
LINEAR:
ANGULAR:

NAME | SIGNATURE | DATE | TITLE: Slab 3

DRAWN

Quadruple-Tank Experimental Setup

APPV'D

MFG

Q.A | MATERIAL: Acrylic | A4

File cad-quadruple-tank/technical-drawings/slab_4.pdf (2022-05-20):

E | E
F | F

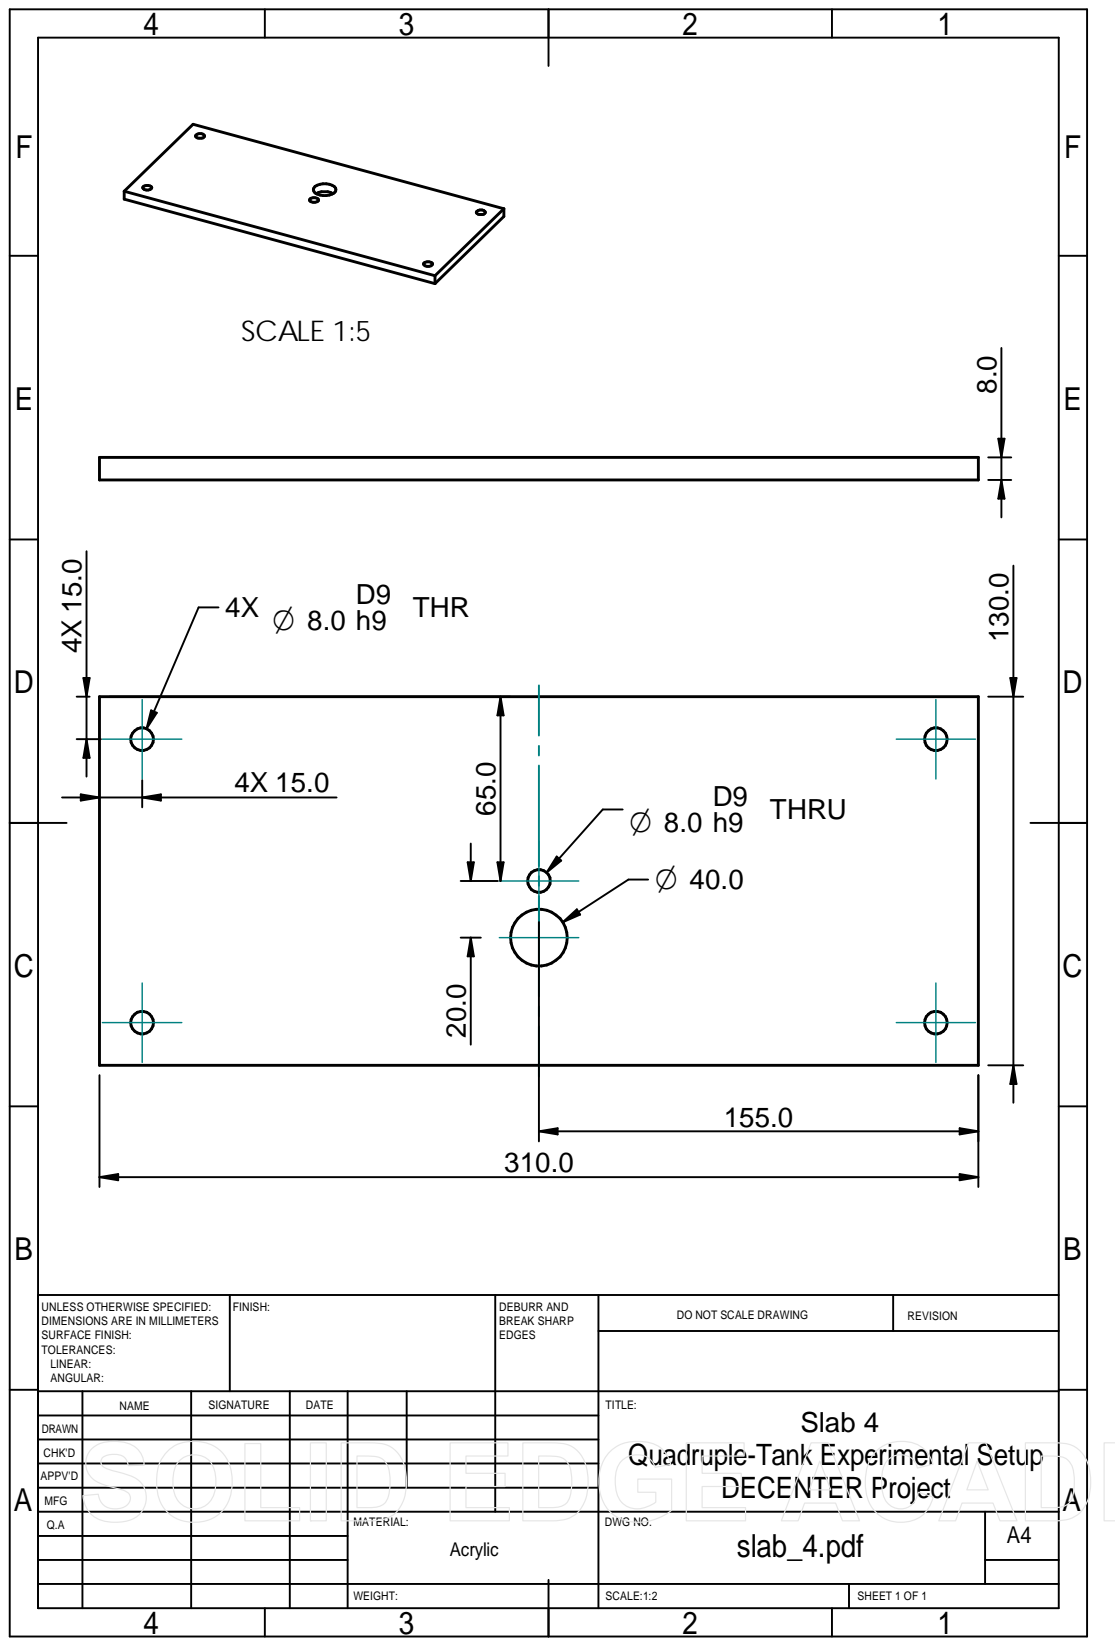
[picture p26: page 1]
FINISH:; DEBURR AND; BREAK SHARP EDGES; DO NOT SCALE DRAWING; REVISION; SCALE:1:2; SHEET 1 OF 1; WEIGHT:; SCALE 1:5; THR; D9 h9 THRU; Acrylic; DECENTER Project

UNLESS OTHERWISE SPECIFIED:
DIMENSIONS ARE IN MILLIMETERS
SURFACE FINISH:
TOLERANCES:
LINEAR:
ANGULAR:

NAME | SIGNATURE | DATE | | | | TITLE: Slab 4 Quadruple-Tank Experimental Setup

DRAWN

CHK'D

APPV'D

MFG

Q.A | | | | MATERIAL: | DWG NO. slab_4.pdf | A4

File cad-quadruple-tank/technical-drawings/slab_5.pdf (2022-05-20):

E | E
F | F

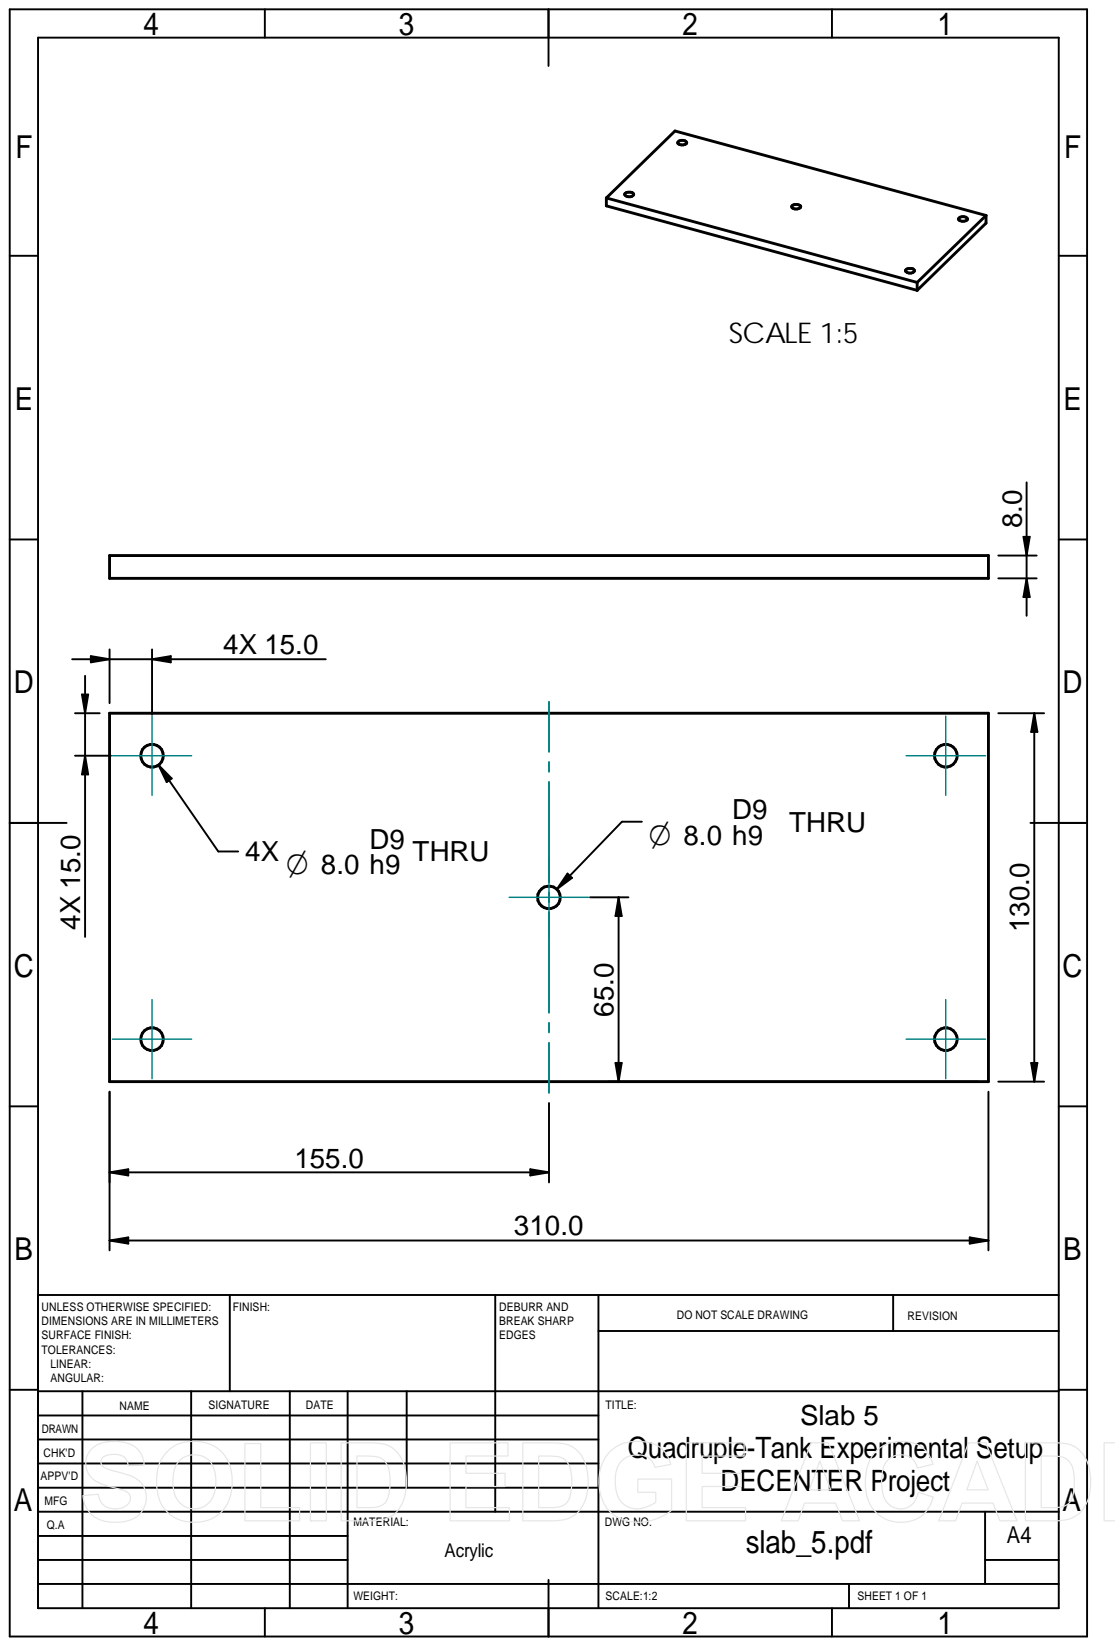
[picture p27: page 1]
FINISH:; DEBURR AND; BREAK SHARP EDGES; DO NOT SCALE DRAWING; REVISION; SCALE:1:2; SHEET 1 OF 1; WEIGHT:; SCALE 1:5; THRU; D9 h9 THRU; Acrylic; DECENTER Project

UNLESS OTHERWISE SPECIFIED:
DIMENSIONS ARE IN MILLIMETERS
SURFACE FINISH:
TOLERANCES:
LINEAR:
ANGULAR:

NAME | SIGNATURE | DATE | | | | TITLE: Slab 5 Quadruple-Tank Experimental Setup

DRAWN

CHK'D

APPV'D

MFG

Q.A | | | | MATERIAL: | DWG NO. slab_5.pdf | A4

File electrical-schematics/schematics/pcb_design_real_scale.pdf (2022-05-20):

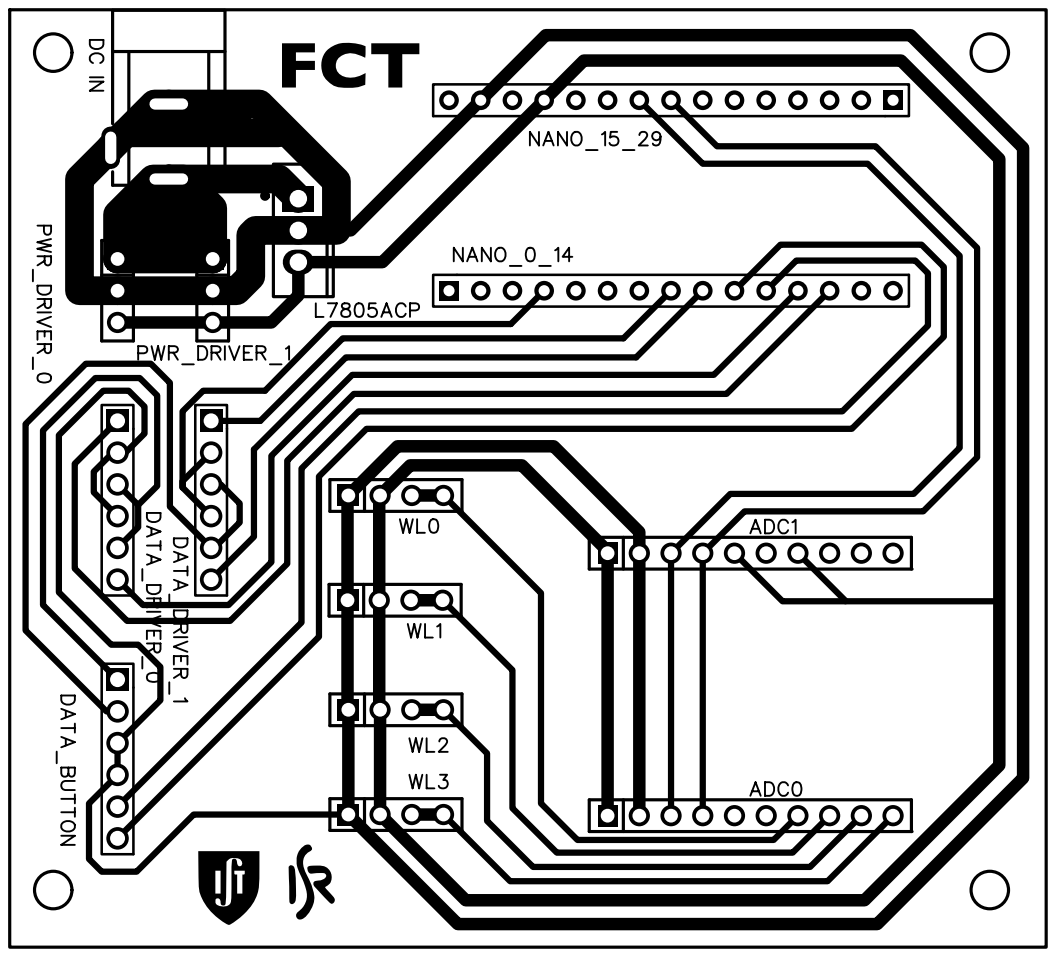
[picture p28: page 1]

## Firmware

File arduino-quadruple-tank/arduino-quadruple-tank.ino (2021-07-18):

/* arduino-quadruple-tank.ino
 * Main file for Arduino Nano of the Quadruple Tank Process for the
 * interface with Simulink via Serial Communication.
 * It receives PWM signal to input to the pumps and brodcasts the
 * voltage values read from the water level sensors.
 * Authors: Leonardo Pedroso, Pedro Batista
 * Institute for Systems and Robotics, Instituto Superior Técnico, 
 * Lisbon, Portugal*/

 /* Developed for project DECENTER (https://decenter2021.github.io/) under MIT license
  * Copyright (c) 2021 DECENTER
  * Permission is hereby granted, free of charge, to any person obtaining 
  * a copy of this software and associated documentation files (the 
  * “Software”), to deal in the Software without restriction, including 
  * without limitation the rights to use, copy, modify, merge, publish, 
  * distribute, sublicense, and/or sell copies of the Software, and to 
  * permit persons to whom the Software is furnished to do so, subject 
  * to the following conditions:
  * The above copyright notice and this permission notice shall be included 
  * in all copies or substantial portions of the Software.
  * THE SOFTWARE IS PROVIDED “AS IS”, WITHOUT WARRANTY OF ANY KIND, EXPRESS 
  * OR IMPLIED, INCLUDING BUT NOT LIMITED TO THE WARRANTIES OF MERCHANTABILITY, 
  * FITNESS FOR A PARTICULAR PURPOSE AND NONINFRINGEMENT. IN NO EVENT SHALL THE 
  * AUTHORS OR COPYRIGHT HOLDERS BE LIABLE FOR ANY CLAIM, DAMAGES OR OTHER 
  * LIABILITY, WHETHER IN AN ACTION OF CONTRACT, TORT OR OTHERWISE, ARISING 
  * FROM, OUT OF OR IN CONNECTION WITH THE SOFTWARE OR THE USE OR OTHER DEALINGS 
  * IN THE SOFTWARE.
  */
 
// Include header file
#include "arduino-quadruple-tank.h"

// ---------- Global variables ----------
// Data broadcast and received from simulink is stored on struct quadrupleData
quadrupleData quadruple;
// Buffer of a single 16 bit word for I2C interface with ADCs
uint16_t bufADC;
// Buffer of a single 8 bit word for serial interface with simulink
uint8_t bufSerial = 0;
// Time of previous received query (used to stop pumps if Simulink times out)
unsigned long prevCom = 0;

// ---------- Setup (runs on startup) ----------
void setup() {
  Serial.begin(9600); // Init serial communication @ 9600 baud
  Wire.begin(); // Init I2C bus for communication with ADCs
  setupPWM10bit(); // Setup 10 bit PWM for pins 9 and 10 (i.e. the actuation pumps)
  pumpInit(); // Setup arduino pins to control the pumps
}

// ---------- Loop (runs on an infinite loop) ----------
/* Information is shared in simulink in the binblock format:
 * https://www.mathworks.com/help/instrument/binblockwrite.html
 * | HEADER | NUMBER OF DIGITS OF #bytes | #bytes | Data in Big Endian | 
 * For water level query:
 * Receives: Header HEADER_REQUEST
 * Brodcasts: | HEADER | '2' | '10' | output_sensor_1 ... output_sensor_4 output_Vcc (2 bytes *5 = 10 bytes)
 * For pump input query:
 * Receives:  | HEADER | '1' | '6' | u1 u2 d3 d4 (2 bytes *2 + 1 byte *2 = 6 bytes)
 */
void loop() {
  // Listen constantly for a query
  if(Serial.available()){
    bufSerial = (uint8_t) Serial.read(); // Read header of request
    if(bufSerial == HEADER_REQUEST){ // If water level is requested
      readTankLevel(); // Read water level sensors
      levelDataSend(); // Broadcast data to simulink
      prevCom = millis(); // Save communication time
    }else if(bufSerial == HEADER){ // If inputs to pumps are received
      bufSerial = 0; // Init buffer to serve as a counter
      while(bufSerial<8){ // Iterate through each of the 6 bytes in the binblock data
        if(Serial.available()){ // Check if nest byte was received
          if(bufSerial <2){ // Ignore the metadata (first 2 bytes) ('16')
            Serial.read();
          }else if(bufSerial == 2){ // Read most significant byte of u[0] (Big Endian format is used for communication)
            quadruple.u[0] = (uint16_t) Serial.read();
            quadruple.u[0] = quadruple.u[0] << 8;
          }else if(bufSerial == 3){ // Read least significant byte of u[0]
            quadruple.u[0] = quadruple.u[0] | (uint16_t) Serial.read();
          }else if(bufSerial == 4){ // Read most significant byte of u[1] (Big Endian format is used for communication)
            quadruple.u[1] = (uint16_t) Serial.read();
            quadruple.u[1] = quadruple.u[1] << 8;
          }else if(bufSerial == 5){ // Read least significant byte of u[1] 
            quadruple.u[1] = quadruple.u[1] | (uint16_t) Serial.read();
          }else if(bufSerial == 6){ // Read d[0]
            quadruple.d[0] = (uint8_t) Serial.read();
          }else if(bufSerial == 7){ // Read d[1]
            quadruple.d[1] = (uint8_t) Serial.read();
          }
          bufSerial ++; // Increment counter
        }
      }
      pumpWrite(); // Write input that was just received to the pumps   
    }  
  }
  // Check if connection was lost
  if(millis()-prevCom > TIMEOUT ){
    quadruple.u[0] = 0; // Stop pumps
    quadruple.u[1] = 0;
    quadruple.d[0] = 0;
    quadruple.d[1] = 0;
    pumpWrite();
  }
}

// ---------- Read water level ----------
/* This function reads the four output voltages of the water level sensors
 * and the Vcc and writes them to the struct quadruple */
void readTankLevel(){
  // Read A0
  I2Cdev::writeWord(ADC0_ADDR,ADC_REG_CONFIG,A0_CONFIG);
  while(1){ // Wait until sample is available
    I2Cdev::readBitW(ADC0_ADDR,ADC_REG_CONFIG,15,&bufADC);
    if(bufADC){ // When bit 15 is true (sample avialable) get sample from ADC
      I2Cdev::readWord(ADC0_ADDR,ADC_REG_CONV,&quadruple.v[0]);
      break;
    } 
  }
  // Read A1
  I2Cdev::writeWord(ADC0_ADDR,ADC_REG_CONFIG,A1_CONFIG);
  while(1){ // Wait until sample is available
    I2Cdev::readBitW(ADC0_ADDR,ADC_REG_CONFIG,15,&bufADC);
    if(bufADC){ // When bit 15 is true (sample avialable) get sample from ADC
      I2Cdev::readWord(ADC0_ADDR,ADC_REG_CONV,&quadruple.v[1]);
      break;
    } 
  }
  // Read A2
  I2Cdev::writeWord(ADC0_ADDR,ADC_REG_CONFIG,A2_CONFIG);
  while(1){ // Wait until sample is available
    I2Cdev::readBitW(ADC0_ADDR,ADC_REG_CONFIG,15,&bufADC);
    if(bufADC){ // When bit 15 is true (sample avialable) get sample from ADC
      I2Cdev::readWord(ADC0_ADDR,ADC_REG_CONV,&quadruple.v[2]);
      break;
    } 
  }
  // Read A3
  I2Cdev::writeWord(ADC0_ADDR,ADC_REG_CONFIG,A3_CONFIG);
  while(1){ // Wait until sample is available
    I2Cdev::readBitW(ADC0_ADDR,ADC_REG_CONFIG,15,&bufADC);
    if(bufADC){ // When bit 15 is true (sample avialable) get sample from ADC
      I2Cdev::readWord(ADC0_ADDR,ADC_REG_CONV,&quadruple.v[3]);
      break;
    } 
  }
  // Read A0 - Vcc
  I2Cdev::writeWord(ADC1_ADDR,ADC_REG_CONFIG,A0_CONFIG);
  while(1){ // Wait until sample is available
    I2Cdev::readBitW(ADC1_ADDR,ADC_REG_CONFIG,15,&bufADC);
    if(bufADC){ // When bit 15 is true (sample avialable) get sample from ADC
      I2Cdev::readWord(ADC1_ADDR,ADC_REG_CONV,&quadruple.v[4]);
      break;
    } 
  }
 }

// ---------- Control pumps ----------
// This function initilizes the io pins that control the pumps
void pumpInit(){
  pinMode(PUMP12_ENB, OUTPUT); // Init enable pin of actuation pumps (active high)
  pinMode(PUMP34_ENB, OUTPUT); // Init enable pin of disturbance pumps (active high)
  digitalWrite(PUMP12_ENB,HIGH);  // Enable actuation pumps
  digitalWrite(PUMP34_ENB,HIGH); // Enable disturnbance pumps
}

// This function writes the received input to the pumps
void pumpWrite(){
  analogWrite10bit(PUMP1_CTRL,quadruple.u[0]); // Write 10 bit pwm to pump 1
  analogWrite10bit(PUMP2_CTRL,quadruple.u[1]); // Write 10 bit pwm to pump 2
  analogWrite(PUMP3_CTRL,quadruple.d[0]); // Write 8 bit pwm to disturbance pump 1
  analogWrite(PUMP4_CTRL,quadruple.d[1]); // Write 8 bit PWM to disturbance pump 2
}

// ---------- Broadcast water level data ----------
/* This function broadcasts the water level information to simulink in a binblock 
 * https://www.mathworks.com/help/instrument/binblockwrite.html
 * Brodcasts: | HEADER | '2' | '10' | output_sensor_1 ... output_sensor_4 output_Vcc (2 bytes *5 = 10 bytes)*/
void levelDataSend(){
  Serial.write(HEADER); // Send binblock header
  Serial.print("210"); // Send metadata (10 bytes sent)
  uint8_t * p; // Address water level data in bytes (Arduino adresses memory in Little Endian)
  p = (uint8_t *) &quadruple.v[0];
  for(uint8_t i = 0;i<sizeof(quadruple.v);i+=2){ // Send bytes in Big Endian
    Serial.write(*(p+i+1)); // Send most significant byte
    Serial.write(*(p+i)); // Send least significant byte
  }
}

// ---------- Configures 10 bit resolution for actuation pump inputs ----------
/* Configure digital pins 9 and 10 for 10-bit PWM output. */
void setupPWM10bit() {
    DDRB |= _BV(PB1) | _BV(PB2);        // Set D9 and D10 as outputs
    TCCR1A = _BV(COM1A1) | _BV(COM1B1)  // Set non-inverting PWM
        | _BV(WGM11);                   // Set mode 14: fast PWM, TOP=ICR1
    TCCR1B = _BV(WGM13) | _BV(WGM12)
        | _BV(CS11);                    // Set clock / 8 
    ICR1 = 0x03ff;                      // Set TOP counter value (10 bits)
}

/* 10-bit version of analogWrite() for pins D9 and D10. */
void analogWrite10bit(uint8_t pin, uint16_t val){
    switch (pin){
        case  9: OCR1A = val; break; // write pwm to D9
        case 10: OCR1B = val; break; // write pwm to D10
    }
}

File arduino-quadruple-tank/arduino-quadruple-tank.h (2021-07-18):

 /* arduino-quadruple-tank.h
 * Header file of Arduino Code of the Quadruple Tank Process for the
 * interface with Simulink via Serial Communication.
 * Authors: Leonardo Pedroso, Pedro Batista
 * Institute for Systems and Robotics, Instituto Superior Técnico, 
 * Lisbon, Portugal*/
 
 /* Developed for project DECENTER (https://decenter2021.github.io/) under MIT license
  * Copyright (c) 2021 DECENTER
  * Permission is hereby granted, free of charge, to any person obtaining 
  * a copy of this software and associated documentation files (the 
  * “Software”), to deal in the Software without restriction, including 
  * without limitation the rights to use, copy, modify, merge, publish, 
  * distribute, sublicense, and/or sell copies of the Software, and to 
  * permit persons to whom the Software is furnished to do so, subject 
  * to the following conditions:
  * The above copyright notice and this permission notice shall be included 
  * in all copies or substantial portions of the Software.
  * THE SOFTWARE IS PROVIDED “AS IS”, WITHOUT WARRANTY OF ANY KIND, EXPRESS 
  * OR IMPLIED, INCLUDING BUT NOT LIMITED TO THE WARRANTIES OF MERCHANTABILITY, 
  * FITNESS FOR A PARTICULAR PURPOSE AND NONINFRINGEMENT. IN NO EVENT SHALL THE 
  * AUTHORS OR COPYRIGHT HOLDERS BE LIABLE FOR ANY CLAIM, DAMAGES OR OTHER 
  * LIABILITY, WHETHER IN AN ACTION OF CONTRACT, TORT OR OTHERWISE, ARISING 
  * FROM, OUT OF OR IN CONNECTION WITH THE SOFTWARE OR THE USE OR OTHER DEALINGS 
  * IN THE SOFTWARE.
  */

// Include open source I2C interface for reading and writing to registers directly
#include "I2Cdev.h" 

// ---------- Define ADC addresses and configuration words ----------
// Check pp. 16-22 of the datasheet of ADS1115 available in the Datasheets folder
/* Write config register (R0x01) - Configure conversion properties and input
 * 15                  / 14:12 / 11:9          / 8                         / 7:5               / 4                         / 3                         / 2                         / 1:0
 * Start: single shot  / AX    / PGA: 6.1444V  / Operating: single shot    / Data rate: 128SPS / Comparator: traditional   / Cmp polarity: active low  / Latching cmp: nonlatching / Cmp: disable
 * 1                   / 1XX   / 000           / 1                         / 100               / 0                         / 0                         / 0                         / 11
 * A0: 100; A1: 101; A2: 110; A3: 111
 * Config single shot A0 - 0xC183; A1 - 0xD183; A2 - 0xE183; A3 - 0xF183
 * Check convertion in bit 15 of config register (R0x01)
 * Read convertion from register R0x00
 * ADC adresses ADC0 - vo_1, vo_2, vo_3, vo_4 and ADC1 - vi 
 */
// Addresses of ADCs
static uint8_t ADC0_ADDR =  0x48; // Reads outputs of water level sensors
static uint8_t ADC1_ADDR =  0x49; // Reads Vcc
// ADC convertion and configuration registers
static uint8_t ADC_REG_CONV =  0x00; // Address of configuration register
static uint8_t ADC_REG_CONFIG =  0x01; // Address of configuration register
// ADC configuration words
static uint16_t A0_CONFIG = 0xC183; // Configuration words for all different analog inputs
static uint16_t A1_CONFIG = 0xD183;
static uint16_t A2_CONFIG = 0xE183;
static uint16_t A3_CONFIG = 0xF183;

// ---------- Define MACROS for serial communication protocol using binblock ----------
#define HEADER '#'
#define HEADER_REQUEST '$'

//  ---------- Define pump pins ----------
#define PUMP1_CTRL 9
#define PUMP2_CTRL 10
#define PUMP12_ENB 7

#define PUMP3_CTRL 5
#define PUMP4_CTRL 6
#define PUMP34_ENB 8

// Define timeout (ms)
#define TIMEOUT 2000

// ---------- Define structs to store data ----------
typedef struct quadrupleData {
    uint16_t v[5]; // output water level sensor (0-3) and input (4) 
    uint16_t u[2]; // input to 2 actuation pumps (10 bit each stored as 16 bit)
    uint8_t d[2]; // input to 2 disturbance pumps (8 bit each)
} quadrupleData;

// ---------- Read water level ----------
// This function reads the four output voltages and the input voltate to the struct quadruple
void readTankLevel();

// ---------- Control pumps ----------
void initPumps();
void pumpWrite();

// ---------- Broadcast water level data ----------
// This function broadcasts the water level information to simulink in a binblock 
// https://www.mathworks.com/help/instrument/binblockwrite.html
void levelDataSend();

// ---------- 16 bit resolution for pump inputs ----------
/* Configure digital pins 9 and 10 for 10-bit PWM output. */
void setupPWM10bit();
/* 10-bit version of analogWrite() for pins D9 and D10. */
void analogWrite10bit(uint8_t pin, uint16_t val);

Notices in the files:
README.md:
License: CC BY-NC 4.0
